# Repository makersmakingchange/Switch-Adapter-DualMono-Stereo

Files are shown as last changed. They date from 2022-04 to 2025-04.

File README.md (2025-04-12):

# Dual Mono Stereo Switch Adapter
The Dual-Mono-Stereo Switch Adapter provides a way to connect two assistive switches with 3.5 mm / 1/8 in mono cables to a single 3.5 mm / 1/8 in stereo input on a compatible assistive technology device. 

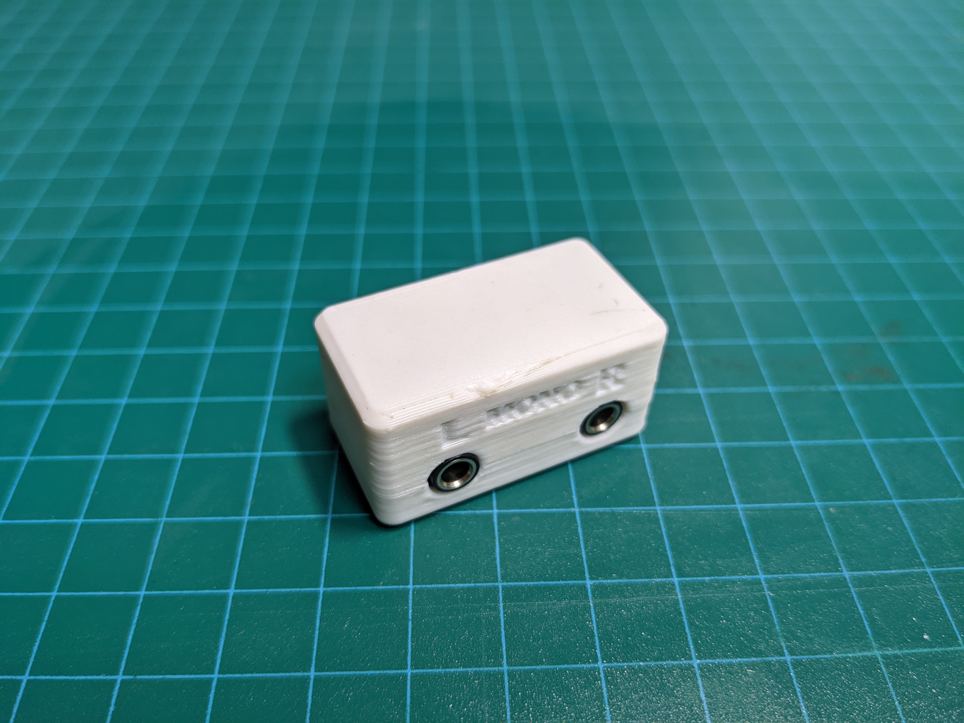
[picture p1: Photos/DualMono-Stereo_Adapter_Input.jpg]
Device Name


## Usage 
To use the Dual Mono-Stereo Adapter, connect the two assistive switches to the Left and Right Inputs on the adapter. Then connect the adapter to the AT device with a stereo male-to-male extension cable.

## More info at
- [Makers Making Change Project Page](https://makersmakingchange.com/project/dual-mono-stereo-adapter/)

## Getting Started

### 1. Order the Off-The-Shelf Components

The [Bill of Materials](/Documentation/Dual-Mono-Stereo_Adapter_BOM_v1.0.csv) lists all of the parts and components required to build the Open Wobble Switch. The main switch component needs to be ordered online. The rest of the off-the-shelf components are also online or may be available in smaller quantities at your local hardware store or dollar store.

### 2. Print the 3D Printable components

3D print the components. Refer to the [3D Printing Guide](/Documentation/Dual-Mono-Stereo_Adapter_3D_Print_Guide_v1.0.pdf).

All of the files and individual print files can be in the [/Build_Files/3D_Printing_Files](/Build_Files/3D_Printing_Files/) folder.

### 3. Assemble the Device

Reference the [Assembly Guide](/Documentation/Dual-Mono-Stereo_Adapter_Assembly_Guide_v1.0.pdf) for the tools and steps required to build each portion.

## Files
### Documentation
| Document             | Version | Link |
|----------------------|---------|------|
| Design Rationale     | 1.0     | [Dual-Mono-Stereo_Adapter_Design_Rationale](/Documentation/Dual-Mono-Stereo_Adapter_Design_Rationale_v1.0.pdf)     |
| Bill of Materials    | 1.0     | [Dual-Mono-Stereo_Adapter_Bill_of_Materials](/Documentation/Dual-Mono-Stereo_Adapter_BOM_v1.0.csv)     |
| 3D Print Guide       | 1.0     | [Dual-Mono-Stereo_Adapter_3D_Print_Guide](/Documentation/Dual-Mono-Stereo_Adapter_3D_Print_Guide_v1.0.pdf)     |
| Assembly Guide       | 1.0     | [Dual-Mono-Stereo_Adapter_Assembly_Guide](/Documentation/Dual-Mono-Stereo_Adapter_Assembly_Guide_v1.0.pdf)     |
| Maker Checklist      | 1.0     | [Dual-Mono-Stereo_Adapter_Maker_Checklist](/Documentation/Dual-Mono-Stereo_Adapter_Maker_Checklist_v1.0.pdf)     |
| User Guide           | 1.0     | [Dual-Mono-Stereo_Adapter_User_Guide](/Documentation/Dual-Mono-Stereo_Adapter_User_Guide_v1.0.pdf)    |
| Changelog            | 1.0     | [Dual-Mono-Stereo_Adapter_ChangeLog](/Documentation/Dual-Mono-Stereo_Adapter_ChangeLog_v1.0.pdf)     |

### Design Files
[CAD Files](/Design_Files)

### Build Files
 - [3D Printing Files](/Build_Files/3D_Printing_Files)
 - [3D Printing Guide](/Documentation/Dual-Mono-Stereo_Adapter_3D_Print_Guide_v1.0.pdf)

## Attribution
Designed and documented by Makers Making Change

### Contributors
 - Jake McIvor, Neil Squire Society / Makers Making Change

## License
Everything needed or used to design, make, test, or prepare the Dual-Mono-Stereo Switch Adapter is licensed under the CERN 2.0 Permissive license https://ohwr.org/project/cernohl/wikis/Documents/CERN-OHL-version-2 (CERN-OHL-P) .

Accompanying material such as instruction manuals, videos, and other copyrightable works that are useful but not necessary to design, make, test, or prepare the Dual-Mono-Stereo Switch Adapter are published under a Creative Commons Attribution-ShareAlike 4.0 license https://creativecommons.org/licenses/by-sa/4.0/ (CC BY-SA 4.0)

<!-- ABOUT MMC START -->
## About Makers Making Change
[Makers Making Change Logo](https://www.makersmakingchange.com/)

Makers Making Change is a program of [Neil Squire](https://www.neilsquire.ca/), a Canadian non-profit that uses technology, knowledge, and passion to empower people with disabilities.

Makers Making Change leverages the capacity of community based Makers, Disability Professionals and Volunteers to develop and deliver affordable Open Source Assistive Technologies.

 - Website: [www.MakersMakingChange.com](https://www.makersmakingchange.com/)
 - GitHub: [makersmakingchange](https://github.com/makersmakingchange)
 - Bluesky: [@makersmakingchange.bsky.social](https://bsky.app/profile/makersmakingchange.bsky.social)
 - Instagram: [@makersmakingchange](https://www.instagram.com/makersmakingchange)
 - Facebook: [makersmakechange](https://www.facebook.com/makersmakechange)
 - LinkedIn: [Neil Squire Society](https://www.linkedin.com/company/neil-squire-society/)
 - Thingiverse: [makersmakingchange](https://www.thingiverse.com/makersmakingchange/about)
 - Printables: [MakersMakingChange](https://www.printables.com/@MakersMakingChange)

### Contact Us
For technical questions, to get involved, or to share your experience we encourage you to [visit our website](https://www.makersmakingchange.com/) or [contact us](https://www.makersmakingchange.com/s/contact).
<!-- ABOUT MMC END -->

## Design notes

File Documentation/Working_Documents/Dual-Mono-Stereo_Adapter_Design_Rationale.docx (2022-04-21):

# Introduction

Some assistive technology devices are equipped with stereo switch input jacks. Generally, these provide the option to connect one or two input devices. These input devices can be a single switch with a 3.5 mm mono plug, a two-input switch with a 3.5 mm stereo plug. To connect two single switches that each has a 3.5 mm mono plug, an adapter is required.

# Research

Commercial adapters are available, but they can be difficult either difficult to source or expensive. Sourcing can also be difficult because there is a type of audio adapter that looks the same but is wired differently.

## Commercial Options

Assistive Technology

- ~~https://cadanat.com/product/mono-to-stereo-adapter/~~~~, $10~~ ~~USD + Shipping~~ (No longer available)
- Stereo-to-mono plug adapter (splitter) - https://www.adaptivetechsolutions.com/cable-kit/ - $31.08 USD, US Shipping only

Audio

3.5 mm TRS to Dual 3.5 mm TSF Stereo Breakout Cable

- https://www.amazon.ca/Hosa-YMM-261-Stereo-Breakout-Cable/dp/B000068O5H, ~$17 CAD

## DIY Options

While the basic schematic is available, we were unable to locate any existing plans for creating a DIY adapter.

## Assistive Device Compatibility

There are several commercial and DIY assistive devices that have a stereo input jack:

- Origin SwiftyTM USB Switch interface
- Origin TapioTM
- Origin HeadMouse
- Darci USB (No longer available, but often still in use)
- LipSync Switch Input Module

# Requirements

## Goals

G01 | The device components should be easy to source.
G02 | The device should be easy to build.
G03 | The device should cost less than the commercially available option, or at least comparable.

## Functional Requirements

F01 | The adapter must have two 3.5 mm female inputs.
F02 | The adapter must have one 3.5 mm stereo output.
F03 | The inputs must be connected to the output pins using the typical AT wiring (i.e., left input tip to output ring, left input sleeve to output sleeve, right input tip to output tip, right input sleeve to output sleeve.)

## Non-functional Requirement

NF01 | Design must be easily manufacturable for a person with skills in soldering, 3D printing, and moderate mechanical handwork
NF02 | Left and right inputs must be labelled.
NF03 | 3D printable components should require minimal support material.

## Constraints

C01 | Single-build cost must be less than $20 CAD.

# Ideation

There are numerous ways that an adapter with the desired schematic could be constructed:

Cables

- 1X 3.5 mm male stereo plug
- 2X 3.5 mm female stereo or mono jack
- Heat-shrink tubing / tape

The cables need to be cut and the wires stripped and then soldered. Shrink tube or tape is then used to reinforce and cover the connection.

All-Female Jacks

- 1X 3.5 mm stereo jack
- 2X 3.5 mm mono or stereo jack
- Wire to solder connections
- Something to hold / contain jacks
- 1 X 3.5 mm extension cable (Male-male)

The jacks need to be soldered together to create the proper connections. The jacks should be mounted inside something to make it easy to plug and unplug cables.

Male Plug and Female Jacks

- 1X 3.5 mm stereo plug
- 2X 3.5 mm mono or stereo jack
- Wire to solder connections
- Something to hold / contain jacks

The jacks and plugs need to be soldered together and contained within an enclosure.

# Conceptual Design

## Schematic

This is not the same as a headphone splitter.

- Left mono tip to stereo ring
- Left mono sleeve to stereo sleeve
- Right mono tip to stereo tip
- Right mono sleeve to stereo sleeve

# Detailed Design – Version 1.0

This version of the device consists of three 3.5 mm stereo jacks that are held in a snap-fit 3d printed enclosure. This configuration was selected to take advantage of an abundance of jacks on hand, and to provide some flexibility in positioning cables (i.e., not requiring the enclosure to connect directly to the device).

## Jack Selection

This particular jack model was selected because a large number were available on-hand from another project (AT Maker Keyswitch) and they were also readily available online (i.e., Amazon https://www.amazon.com/Gikfun-Stereo-Female-Connector-Arduino/dp/B01KFP0M4S). These are now no longer available, so an equivalent part was found on DigiKey.

ID | MPN | Manufacturer | Cost | Link
1 | SJ1-3535NG | CUI Devices | $1.91 | https://www.digikey.ca/en/products/detail/cui-devices/SJ1-3535NG/738699
2 | SJ1-3533NG | CUI Devices | $1.86 | https://www.digikey.ca/en/products/detail/cui-devices/SJ1-3533NG/738701
3

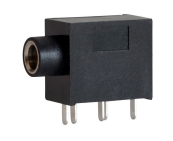
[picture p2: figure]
Picture of a SJ1-353NG audio switch jack. It has a smooth jack portion and 5 leads.

Figure 1: SJ1-353NG

Source: Datasheet (https://www.cuidevices.com/product/resource/sj1-353xng.pdf)

## Enclosure

A simple two-part, 3d-printed, snap-fit enclosure was designed to cover and contain the switch jacks.

# Opportunities for Improvement

- This design is cost-effective if the jacks are already on-hand or are purchased as part of a larger order. A single-one off build that incurs shipping charges will be more expensive than the commercial option from Amazon.
- It may be beneficial to include the wiring diagram directly on the 3d printed enclosure somehow to aid the maker.
- The design should be easy to modify to accommodate a different model of switch jack.

© 2022 by Neil Squire / Makers Making Change. This work is licensed under the CC BY SA 4.0 License: http://creativecommons.org/licenses/by-sa/4.0 Files available at https://makersmakingchange.com/project/dual-mono-stereo-adapter/ Page 1 of 1

V1.0 | APRIL 2022 Dual Mono-Stereo Adapter Design Rationale

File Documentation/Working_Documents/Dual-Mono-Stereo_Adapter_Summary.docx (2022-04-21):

# Title

Dual Mono-Stereo Adapter

# Subtitle

Adapter for connecting two mono switches to a single stereo input.

### Overview

The Dual Mono-Stereo Adapter provides a way to connect two assistive switches with 3.5 mm / 1/8” mono cables to a single 3.5 mm / 1/8” stereo input on a compatible assistive technology device. This device is functionally equivalent to a 3.5 mm TRS to Dual 3.5 mm TSF Stereo Breakout Cable (Amazon Link (https://www.amazon.ca/gp/product/B000068O5H), ~$16).

### Usage

To use the Dual Mono-Stereo Adapter, connect the two assistive switches to the Left and Right Inputs on the adapter. Then use a stereo male-to-male audio cable to connect the adapter to the AT device's 3.5 mm stereo input.

This is also suitable for use with the LipSync Switch Input Module (https://makersmakingchange.com/project/lipsync-switch-input-module/).

### Commercial Alternatives

This is equivalent a 3.5 mm TRS to Dual 3.5 mm TSF Stereo Breakout Cable (Amazon Link (https://www.amazon.ca/gp/product/B000068O5H)).

https://cadanat.com/product/mono-to-stereo-adapter/

### Build Instructions

The Dual-Mono-Stereo Adapter consists of some electronic components and a 3D printed enclosure. Detailed build instructions can be found in the GitHub link.

#### Skills Required

- 3D Printing
- Soldering

#### Tools Required

- Soldering Iron
- Solder
- Wire Strippers

#### Components

- 1X 3D printed Case Top
- 1X 3D printed Case Bottom
- 3X Stereo Jacks (https://www.digikey.ca/en/products/detail/cui-inc/SJ1-3535NG/738699)
- 4x 25 mm (1”) lengths of wire

#### 3D Printing

Print the top and bottom enclosure pieces following the 3D printing guide.

### Attribution

Design by Makers Making Change

# Dual Mono-Stereo Switch Adapter

## Links

MMC Device Library: https://makersmakingchange.com/project/dual-mono-stereo-adapter/

GitHub: https://github.com/makersmakingchange/Spinning-Light-Wand-Adaptation

## Overview

The Dual Mono-Stereo Adapter provides a way to connect two assistive switches with 3.5 mm / 1/8” mono cables to a single 3.5 mm / 1/8” stereo input on a compatible assistive technology device. This device is functionally equivalent to a 3.5 mm TRS to Dual 3.5 mm TSF Stereo Breakout Cable (Amazon Link (https://www.amazon.ca/gp/product/B000068O5H), ~$16).

© 2022 by Neil Squire / Makers Making Change. This work is licensed under the CC BY SA 4.0 License: http://creativecommons.org/licenses/by-sa/4.0 Files available at https://makersmakingchange.com/project/dual-mono-stereo-adapter/ Page 1 of 2

V1.0 | APRIL 2022 Dual Mono-Stereo Adapter Summary

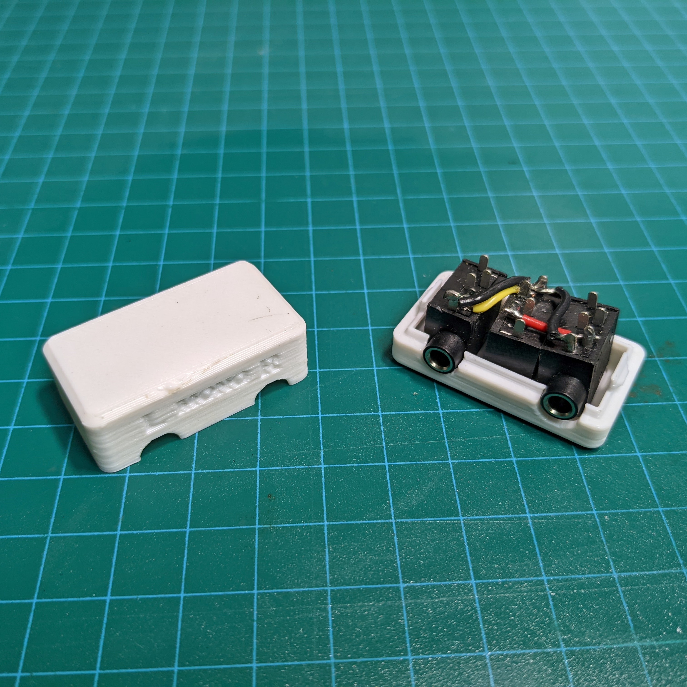
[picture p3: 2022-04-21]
Photos/DualMono-Stereo_Adapter_Open.jpg

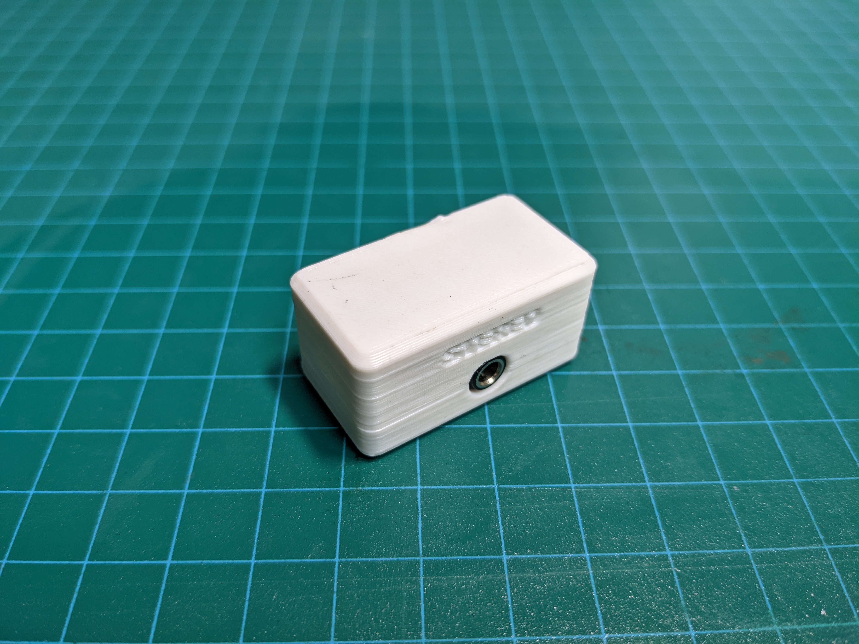
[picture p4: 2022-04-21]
Photos/DualMono-Stereo_Adapter_Output.jpg

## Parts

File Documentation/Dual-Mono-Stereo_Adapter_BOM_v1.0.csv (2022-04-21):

Device: Dual Mono-Stereo Adapter |  | Total Cost | Total Print time (hr) | Total filament (g)
Version: V1.0 | Date Created: 4/20/2021 | $5.98 | 0.63 | 6.37
Commercial Parts
Part type (Electrical, Mechanical, Sanitization, etc) | Part Name | Qty Needed | Pkg Qty | $ / pkg | $/unit | Price for qty needed | Link
Electrical | Stereo Jack | 3 | 1 | $1.94 | $1.94 | $5.82 | https://www.digikey.ca/product-detail/en/cui-inc/SJ1-3535NG/CP1-3535NG-ND/738699
 |  |  |  |  |  |  | https://www.amazon.ca/gp/product/B01M1PAL43/ref=ppx_yo_dt_b_search_asin_title?ie=UTF8&psc=1
3D Printed Parts ESTIMATED PRICING USING 1KG ROLL COST: | $25.00
Part | Description | Quantity Needed | TOTAL Mass (g) | Estimated Price | Print Time (Min) | Link
Top Enclosure |  | 1 | 3.84 | $0.10 | 22
Bottom Enclosure |  | 1 | 2.53 | $0.06 | 16
 |  |  |  | $-
 |  |  |  | $-
 |  |  |  | $-
 |  |  | Total Print Cost: | $0.16
Tools for Assembly
Alternatives (if there are other sources for some parts link them below)
Part and description | Link

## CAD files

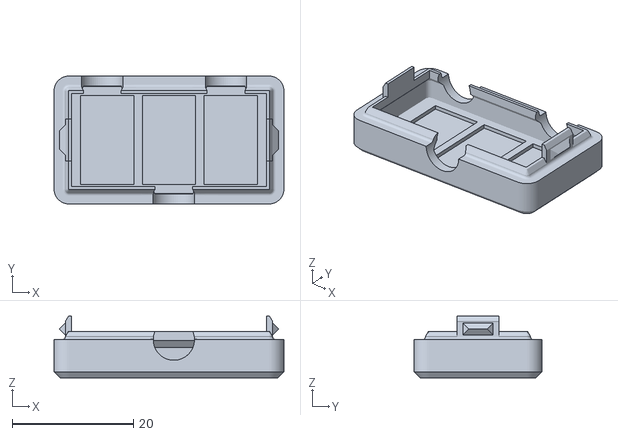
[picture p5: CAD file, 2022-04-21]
Build_Files/3D_Printing_Files/Bottom.stl
37.9 x 21.1 x 10.2

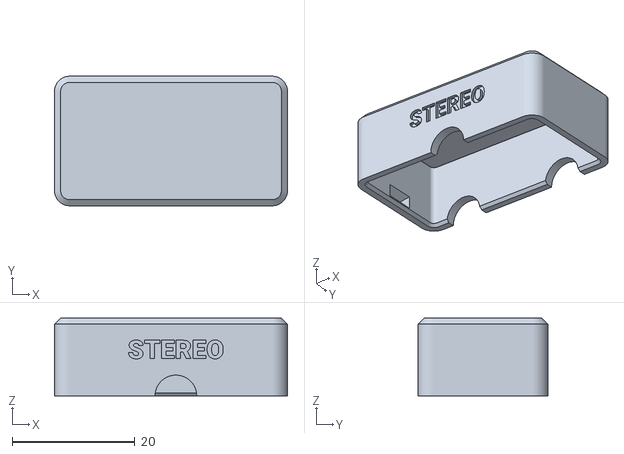
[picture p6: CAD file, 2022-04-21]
Build_Files/3D_Printing_Files/Top.stl
37.9 x 21.1 x 12.7

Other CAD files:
Design_Files/SwitchAdapter-Dual-Mono-Stereo_v11.f3z

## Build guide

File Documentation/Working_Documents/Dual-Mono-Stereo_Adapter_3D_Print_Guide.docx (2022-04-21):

# 3D Printing Summary

Metric
Total Print Time (min) | 34
Total Number of Components | 2
Typical Total Mass (g) | 6.3
Typical Number of Print Setups | 1

# 3D Printing Settings

Print File Name | Qty | Total Print Time (hr:min) | Mass (g) | Infill (%) | Support(Y/N) | Layer Height/ Nozzle Diameter(mm) | Notes (orientation, special settings, etc)
Top.stl | 1 | 0:22 | 3.8 | 20 | N | 0.2/0.4 | -
Bottom.stl | 1 | 0:16 | 2.5 | 20 | N | 0.2/0.4 | - Print in given orientation

# Customization Options

The user can request different colours for the top and/or bottom enclosure.

# Post-Processing

Clean up any stringing and smooth any sharp edges. Can optionally use a marker or paint to make the labels more readable.

# Examples of Quality Prints:

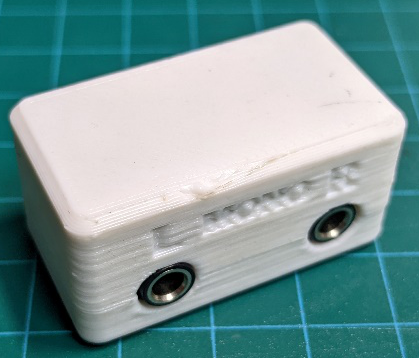
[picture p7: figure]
Picture of 3d printed enclosure input side
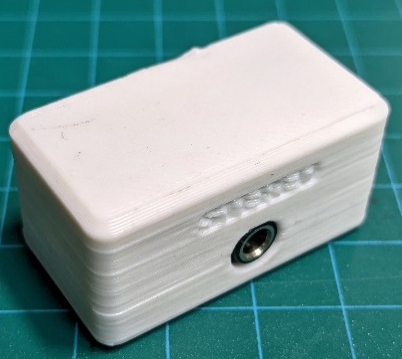
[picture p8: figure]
Picture of 3d printed enclosure output side

© 2022 by Makers Making Change. This work is licensed under the CC BY SA 4.0 License: http://creativecommons.org/licenses/by-sa/4.0 Files available at https://makersmakingchange.com/project/dual-mono-stereo-adapter/ Page 1 of 2

V1.0 | APRIL 2022 Dual Mono-Stereo Adapter 3D Printing Guide

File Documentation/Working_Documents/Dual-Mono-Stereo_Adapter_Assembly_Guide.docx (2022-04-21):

# Required Components

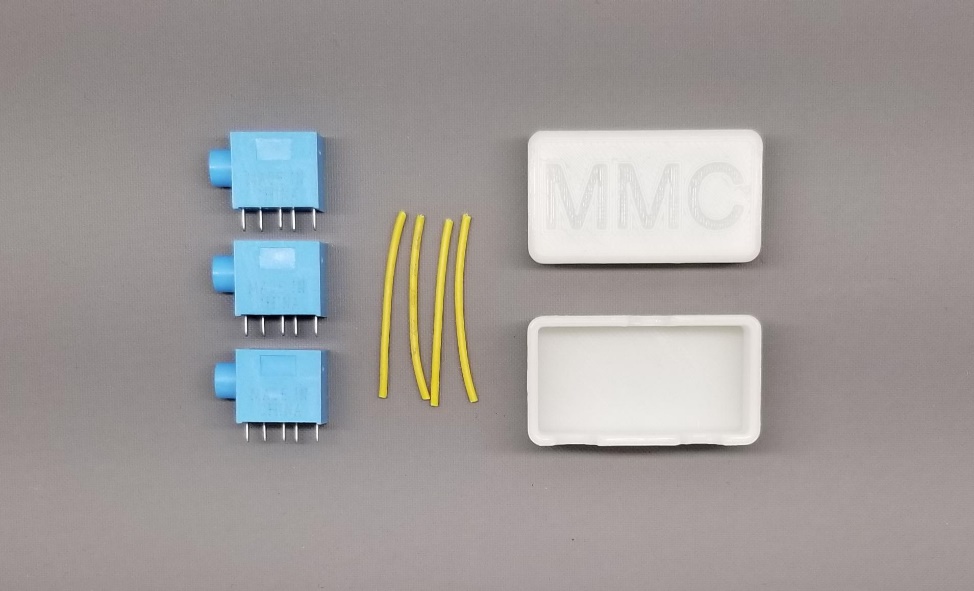
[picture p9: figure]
Picture of adapter components. The three stereo switch jacks are labelled number 1. The four lengths of wire are labelled 2. The one 3d printed enclosure top is labelled 4. The one 3d printed bottom enclosure is labelled 4.

4 3 2 1 | BOM 1. Three Stereo Jacks 2. Four 3 cm Wires 3. 3D Printed Bottom 4. 3D Printed Top

# Required Tools

- Soldering Iron
- Solder
- Wire strippers
- Flush cutters

# Required Personal Protective Equipment (PPE)

- Safety Glasses

# Assembly Instructions

## Step 1

Place the stereo Jacks in the bottom enclosure with their prongs facing outward. Ensure each jack is facing the correct direction, so the outlet lines up with the holes.

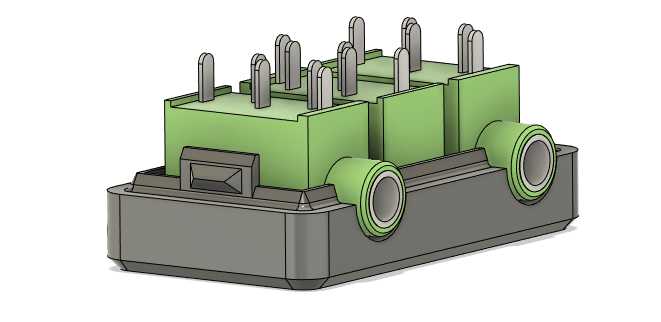
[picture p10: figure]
Diagram of enclosure bottom with three jacks place inside. The jacks are protruding through the case and the solder leads are oriented upwards.

## Step 2

Solder the wires into place according to the black wires shown in the image. Trim any excess wire with flush cutters.

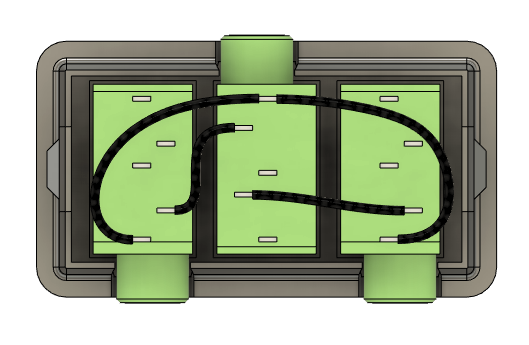
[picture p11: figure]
Diagram of adapter wiring. The view is oriented looking down towards the bottom enclosure. The single output jack is oriented to the top and the two input jacks are oriented towards the bottom. Each jack has 5 leads. Connection 1: the bottom most lead on the left input jack connects to the top lea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

## Step 3

Snap the top enclosure onto the bottom enclosure. Ensure the holes line up with the jack outlets.

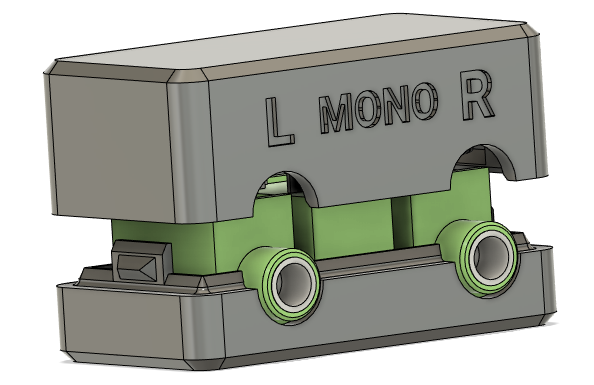
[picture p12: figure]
Diagram of enclosure assembly. On the top enclosure, the input side has two semi-circular notches for the input jacks. The top part of the enclosure is pushed down on to the bottom enclosure.

© 2022 by Makers Making Change. This work is licensed under the CC BY SA 4.0 License: http://creativecommons.org/licenses/by-sa/4.0 Files available at https://makersmakingchange.com/project/dual-mono-stereo-adapter/ Page 1 of 1

V1.0 | APRIL 2022 Dual Mono-Stereo Adapter Assembly Guide

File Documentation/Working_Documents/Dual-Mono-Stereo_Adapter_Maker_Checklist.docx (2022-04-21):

# Maker To Do List

- Ask User for preferences (e.g., enclosure color, any special requests, etc.)
- Order Stereo Jacks from the BOM link
- 3D print the enclosure
- Assemble the adapter
- Print User Quick Guide

# Items to Give to User

- Assembled Dual Mono-Stereo Adapter Device
- Printed User Quick Guide

© 2022 by Makers Making Change. This work is licensed under the CC BY SA 4.0 License: http://creativecommons.org/licenses/by-sa/4.0 Files available at https://makersmakingchange.com/project/dual-mono-stereo-adapter/ Page 1 of 1

V1.0 | APRIL 2022 Dual Mono-Stereo Adapter Maker Checklist

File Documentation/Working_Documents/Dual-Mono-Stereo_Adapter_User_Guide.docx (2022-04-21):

## Introduction

The Dual Mono-Stereo Adapter enables two separate switches to be connected into a single stereo input. This is equivalent to a 3.5 mm TRS to Dual 3.5 mm TSF Stereo Breakout Cable.

## Features

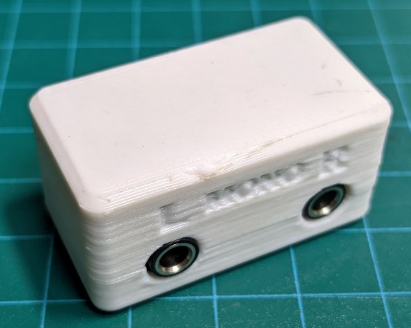
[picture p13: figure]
Picture of 3d printed enclosure input side with two jack holes. Left mono input is on the left, right mono input is on the right.
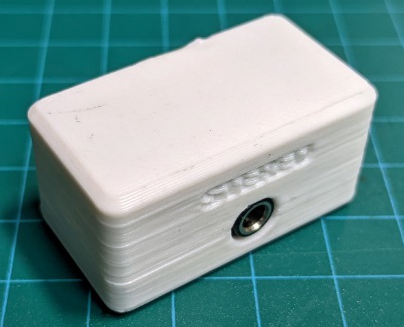
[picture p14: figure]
Picture of 3d printed enclosure out side with one jack hole. Stereo output jack is located in the center.

Left Mono Input Right Mono Input Single Stereo Output

## Usage

Connect the switches to the desired left of right input jack. Use a 3.5 mm extension cable to connect the output to the input on the assistive device.

## Compatibility

Switches: Assistive switches and devices with 3.5 mm output plug.

AT Devices: Assistive devices with 3.5 mm stereo input plug (e.g., Origin SWIFTY, Origin TAPIO, Origin HEADMOUSE, Darci USB)

## Specifications

Mass | 12 g
Dimensions (length x width x height) | 38 mm X 21 mm X 19 mm

## Cleaning

The Dual Mono-Stereo Adapter can be wiped down with sanitizing cleaners.

- Do not submerge in liquid.
- Do not expose to high heat.

© 2022 by Neil Squire / Makers Making Change. This work is licensed under the CC BY SA 4.0 License: http://creativecommons.org/licenses/by-sa/4.0 Files available at https://makersmakingchange.com/project/dual-mono-stereo-adapter/ Page 1 of 1

V1.0 | APRIL 2022 Dual Mono-Stereo Adapter user Quick Guide

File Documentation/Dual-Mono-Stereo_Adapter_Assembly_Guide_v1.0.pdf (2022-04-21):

V1.0 | APRIL 2022

# Dual Mono-Stereo Adapter

# ASSEMBLY GUIDE

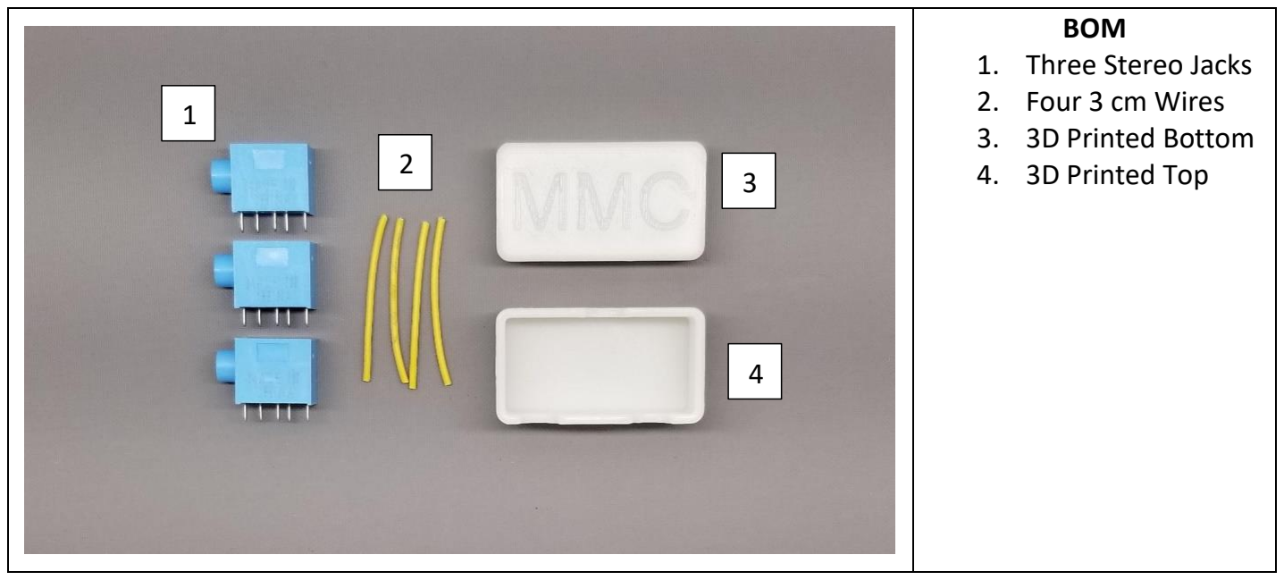
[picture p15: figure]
BOM 1. Three Stereo Jacks 2. Four 3 cm Wires 3. 3D Printed Bottom 4. 3D Printed Top

© 2022 by Makers Making Change. This work is licensed under the CC BY SA 4.0 License: http://creativecommons.org/licenses/by-sa/4.0
Files available at https://makersmakingchange.com/project/dual-mono-stereo-adapter/ (https://makersmakingchange.com/?post_type=project&p=14336&preview=true) | Page 1 of 3

# Required Components

# Required Tools

## - Soldering Iron - Solder - Wire strippers - Flush cutters

# Required Personal Protective Equipment (PPE)

## - Safety Glasses

# ASSEMBLY GUIDE

# Assembly Instructions

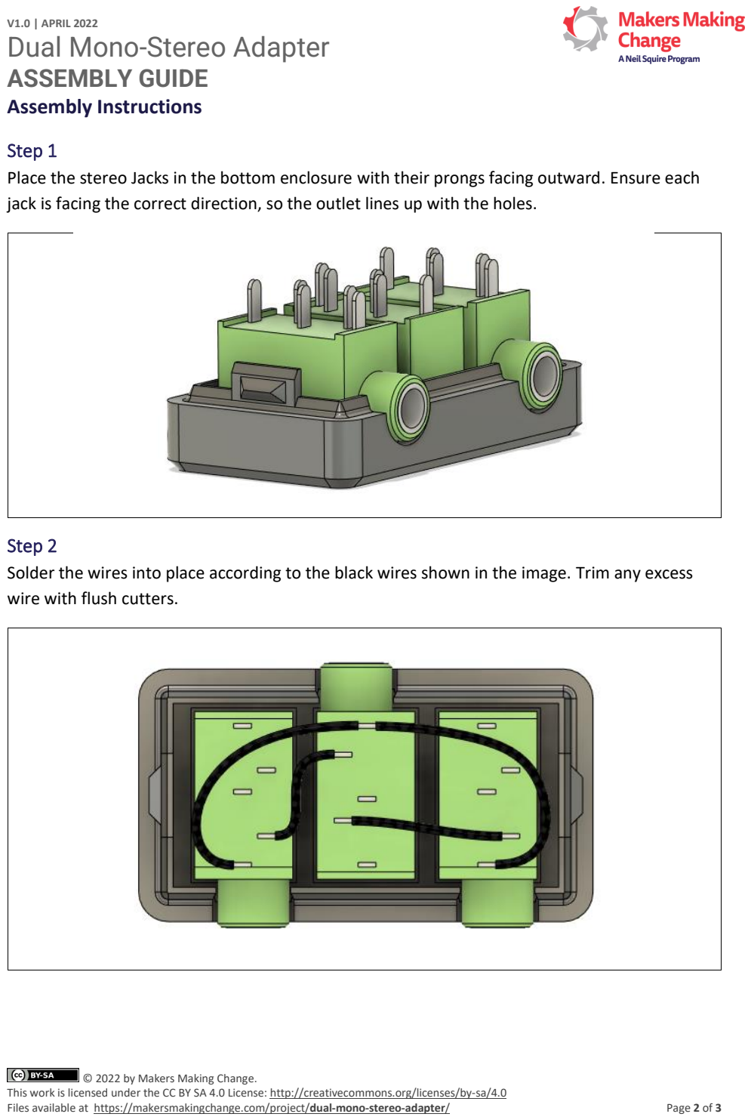
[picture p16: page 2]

Files available at https://makersmakingchange.com/project/dual-mono-stereo-adapter/ (https://makersmakingchange.com/?post_type=project&p=14336&preview=true) | Page 2 of 3

## Step 1

Place the stereo Jacks in the bottom enclosure with their prongs facing outward. Ensure each jack is facing the correct direction, so the outlet lines up with the holes.

## Step 2

Solder the wires into place according to the black wires shown in the image. Trim any excess wire with flush cutters.

# ASSEMBLY GUIDE

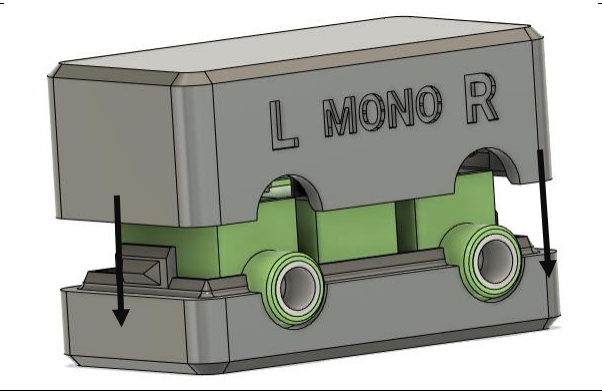
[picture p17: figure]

Files available at https://makersmakingchange.com/project/dual-mono-stereo-adapter/ (https://makersmakingchange.com/?post_type=project&p=14336&preview=true) | Page 3 of 3

## Step 3

## Snap the top enclosure onto the bottom enclosure. Ensure the holes line up with the jack

outlets.

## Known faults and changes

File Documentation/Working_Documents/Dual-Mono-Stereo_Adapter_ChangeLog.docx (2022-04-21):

# Version 1.0 | Date 2022-Apr-06

- Adjusted labels
- Creation of all supporting documentation

# Version 0.1 | 2021-May-05

- Initial version created.

© 2022 by Makers Making Change. This work is licensed under the CC BY SA 4.0 License: http://creativecommons.org/licenses/by-sa/4.0 Files available at https://makersmakingchange.com/project/dual-mono-stereo-adapter/ Page 1 of 1

V1.0 | APRIL 2022 Dual Mono-Stereo Adapter changelog
